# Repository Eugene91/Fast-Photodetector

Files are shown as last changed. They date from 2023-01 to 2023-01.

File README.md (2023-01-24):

# Fast-Photodetector
Kicad design of high speed photodetector (~200 MHz) that is based on OPA 857 Transimpedance circuit. 
## Few notes:
- Circuit is designed and tested with Hamamatsu [Hamamatsu S5972](https://www.hamamatsu.com/eu/en/product/type/S5972/index.html) photodiodes  but maybe used with other photodiodes with similar or larger capacitance (note that the bandwidth may be photodiode limited in this case). 
- Circuit is supplied by external 9-15V voltage via pin connectors. 
- The datasheet of OPA 857 suggests installing shunting capacitance in parallel with R3 with a capacitance of 0.1 pF. 
However the experiment did not show the much performance difference in the presence of the capacitance.
- The first version of the photodetector is depicted below.

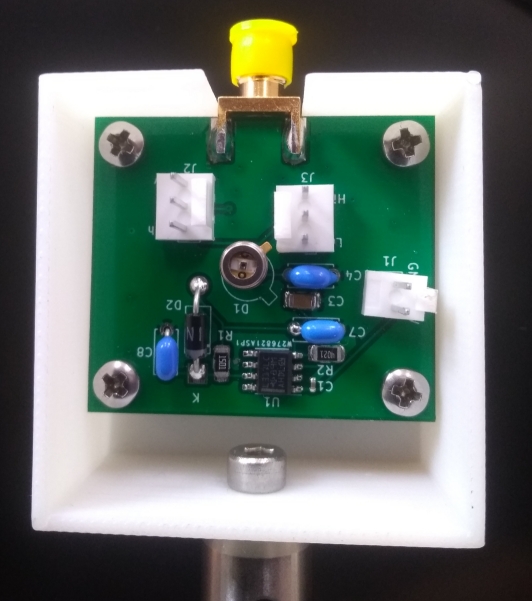
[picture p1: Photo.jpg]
Assembled Photodetectors


Some changes were introduced in the current version:
- Through hole capacitors are replaced SMD components.
- All passive SMD components are replaced with 1206 case for convenience
- 0.1 pF capacitance is removed.

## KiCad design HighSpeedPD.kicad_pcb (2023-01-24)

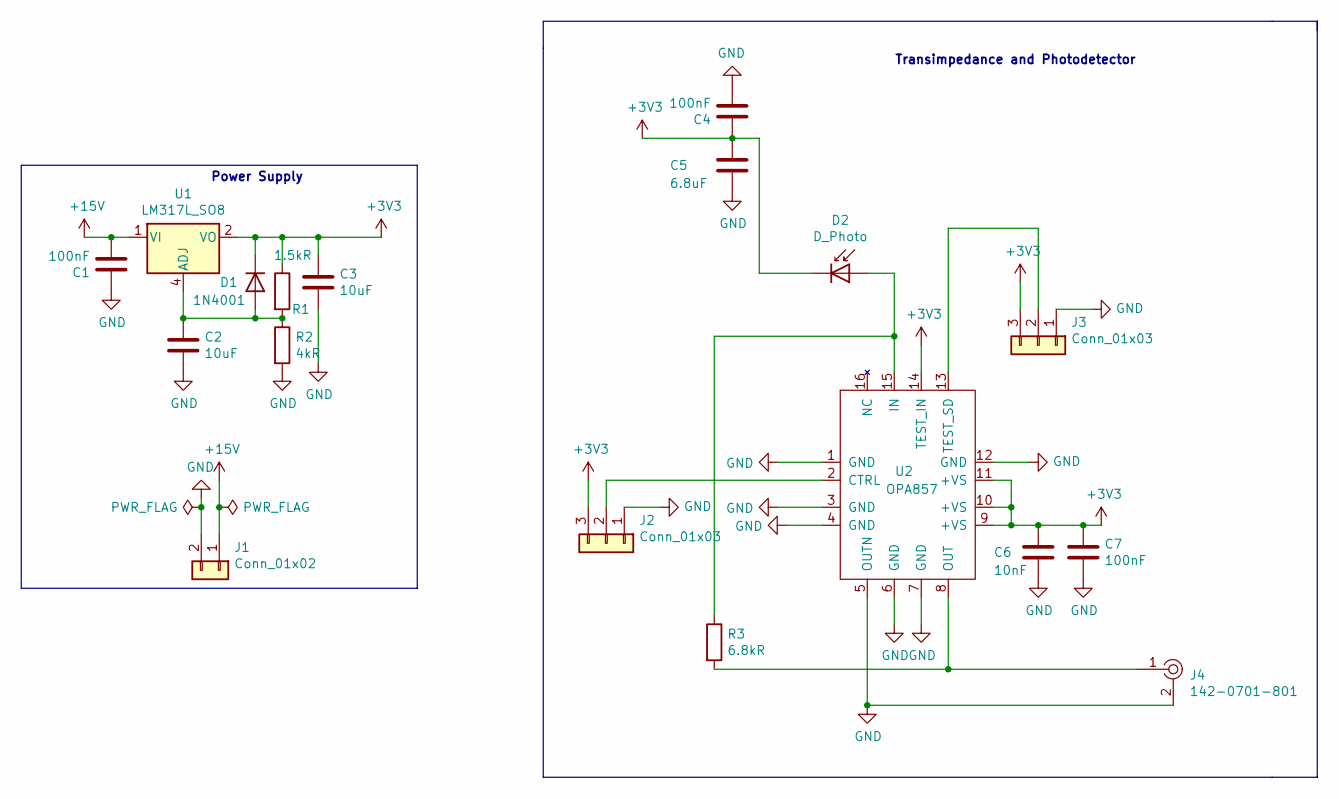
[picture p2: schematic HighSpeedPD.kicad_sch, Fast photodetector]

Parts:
C1, C4, C7: 100nF; C_1206_3216Metric
C2, C3: 10uF; C_1206_3216Metric
C5: 6.8uF; C_1206_3216Metric
C6: 10nF; C_1206_3216Metric
D1: 1N4001; D_DO-41_SOD81_P10.16mm_Horizontal
D2: D_Photo; TO-18-3
J1: Conn_01x02; PinHeader_1x02_P2.54mm_Vertical
J2, J3: Conn_01x03; PinHeader_1x03_P2.54mm_Vertical
J4: 142-0701-801; RF_SMA_BoardEdge_142-0701-801; MPN 142-0701-801; Digi-Key_PN J502-ND
R1: 1.5kR; R_1206_3216Metric
R2: 4kR; R_1206_3216Metric
R3: 6.8kR; R_1206_3216Metric
U1: LM317L_SO8; SOIC-8_3.9x4.9mm_P1.27mm
U2: OPA857; VFQFN-16-1EP_3x3mm

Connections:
+3V3: C3.1, C4.1, C5.1, C6.1, C7.1, D1.1 (K), D2.1 (K), J2.3, J3.3, R1.1, U1.2 (VO), U1.3 (VO), U1.6 (VO), U1.7 (VO), U2.9 (+VS), U2.10 (+VS), U2.11 (+VS), U2.14 (TEST_IN)
+15V: C1.2, J1.1, U1.1 (VI)
GND: C1.1, C2.2, C3.2, C4.2, C5.2, C6.2, C7.2, J1.2, J2.1, J3.1, J4.2, R2.2, U2.1 (GND), U2.3 (GND), U2.4 (GND), U2.5 (OUTN), U2.6 (GND), U2.7 (GND), U2.12 (GND)
unnamed: C2.1, D1.2 (A), R1.2, R2.1, U1.4 (ADJ)
unnamed: D2.2 (A), R3.1, U2.15 (IN)
unnamed: J2.2, U2.2 (CTRL)
unnamed: J3.2, U2.13 (TEST_SD)
unnamed: J4.1, R3.2, U2.8 (OUT)

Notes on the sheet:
Transimpedance and Photodetector
Power Supply

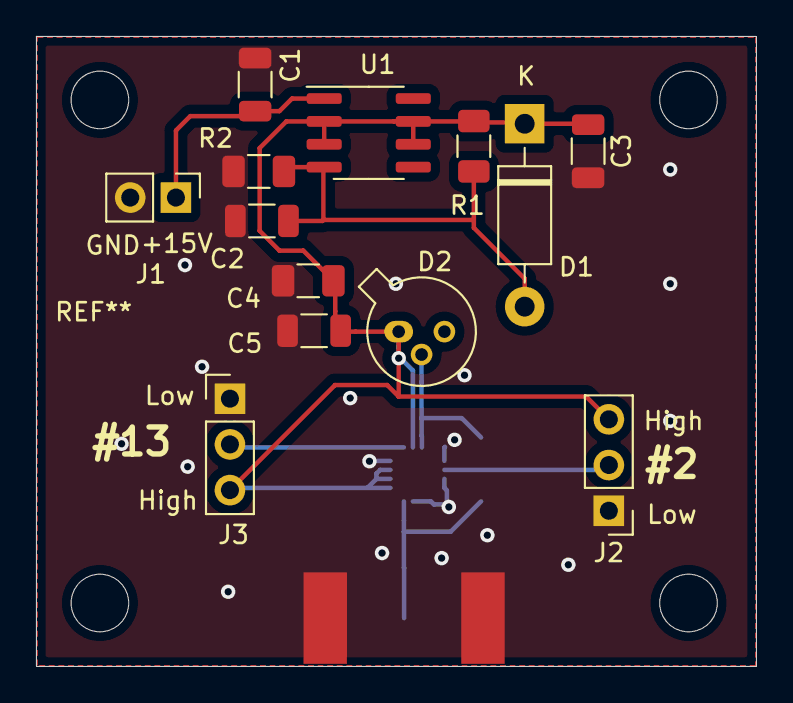
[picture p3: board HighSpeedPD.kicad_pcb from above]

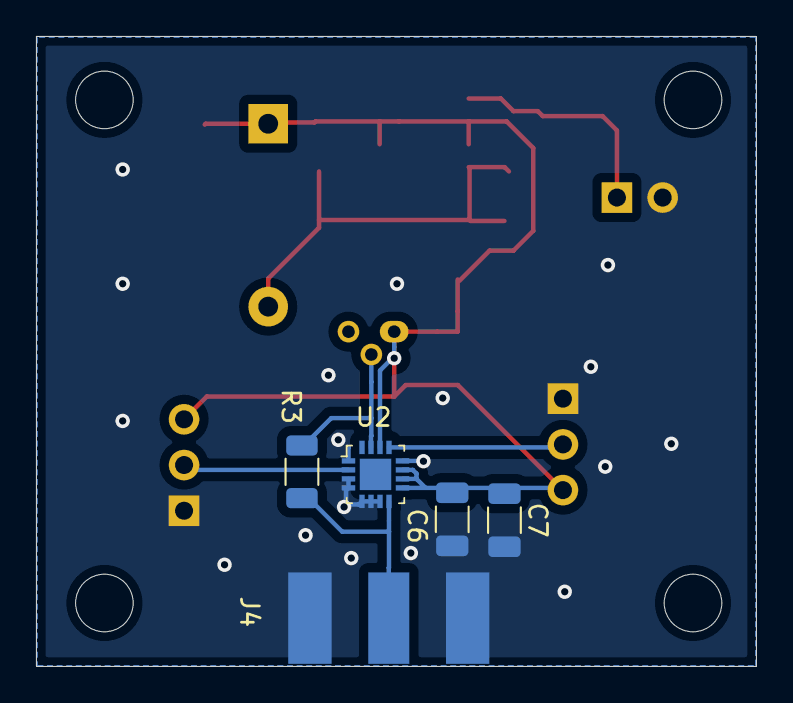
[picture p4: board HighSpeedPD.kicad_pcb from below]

Board: 2 copper layers, 40.0 x 35.0 mm, 18 parts (5 on the bottom side), 8 nets.
